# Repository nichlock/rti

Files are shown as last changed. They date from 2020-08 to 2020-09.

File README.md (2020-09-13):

# Open Source RTI

Source for the software, hardware and physical construction of a Reflectance Transformation Imager for George Washington University.

For information on the contents of the system, see [our Wiki](https://github.com/nichlock/rti/wiki). For more on the build and usage, [see the docs folder](../../tree/master/docs).

This repository contains our RTI's hardware and software implementation, and includes the source and documentation for:
1. A custom designed Arduino Mega shield to control the dome, which powers a three-color LED matrix and triggers the cameras.
2. Another custom circuit board which holds all three colors of LEDs in a smaller area than if we had three separate boards, allowing for a more compact dome.
3. The program to control the dome, with a serial or GUI control interface.
4. The GUI within the above program, which enables easy control over the whole system with no need for technical knowledge. See more about the GUI on our [system overview page](https://github.com/nichlock/rti/wiki/About-the-System#software-and-gui).

Image of the main dome

Image of the software's home screen.

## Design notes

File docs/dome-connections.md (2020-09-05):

### Contents

- [About the Wiring Scheme](#About-the-Wiring-Scheme)
- [How to Wire the Dome Matrix](#How-to-Wire-the-Dome-Matrix)
  - [Getting Parts](#getting-parts)
- [The Process](#The-Process)
  - [1. Get Things Together](#1-Get-Things-Together)
  - [2. Solder Wires on LED Boards](#2-Solder-Wires-on-LED-Boards)
  - [3. Install LED Boards](#3-Install-LED-Boards)
  - [4. Measure and Cut Wires and Build Connectors](#4-Measure-and-Cut-Wires-and-Build-Connectors)

---

# About the Wiring Scheme

If you're familiar with LED arrays, you can skip to [How to Wire the Dome](#how-to-wire-the-dome-Matrix).

## Common Matrices

When creating an array of LEDs, the common choice is to create a matrix of LEDs. This matrix allows us to control lots of LEDs with few control lines, meaning less hardware is needed to connect and drive the matrix. Matrixes are represented in rectangular configurations, but they can take any shape needed, and in our case, that shape is of circular rings that climb up a semi-sphere.

A commonality of RTI dome designs is to have 8 rings of 8 LEDs - and that's no coincidence. These domes are designed after an 8x8 LED matrix, which has 64 LEDs in it. One way to think of these matrixes is as a grid with units used to refer to any one position. The position (0, 0) is the first row, first column, while the position (5, 6) is the one cell that is both in the fifth column and sixth row.

Take a look at this picture. Although it may not look like a grid, it's got the same concept - the LEDs, represented with the arrow symbols, are all connected to exactly one column and one row. The columns and rows cross in this picture but they aren't connected. By "activating" column 5 and row 6, the LED at the position (5, 6) will turn on.

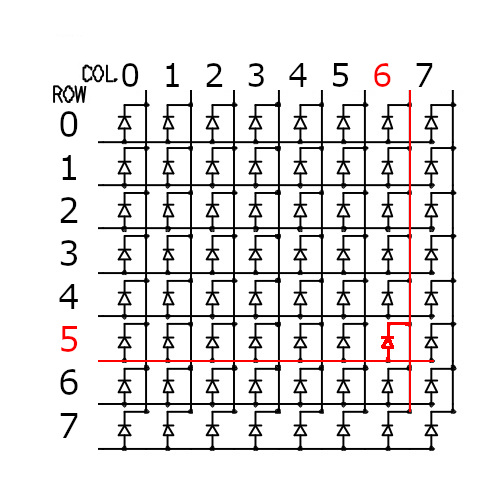
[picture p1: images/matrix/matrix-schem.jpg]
Matrix schematic
|  |
| :--- |
| (Original image credit to Arduino: https://www.arduino.cc/en/Tutorial/RowColumnScanning) |

Something to note about these is that in the real world, we can activate multiple LEDs in this matrix either one column at a time or one row at a time. If we tried to activate two LEDs diagonal to each other, say (0, 0) and (1, 1), we would end up with (0, 1) and (1, 0) also lit up.

## Our System

That's what it looks like for a single color array, but we need three colors: ultraviolet, white, and infrared. All we need is three more copies of the 8x8 design all connected - in three dimensions, you can think of stacking three 8x8 grids on top of each other. For all three stacked matrices, if the columns are kept as three separate groups of 8, the 8 rows can be connected across the layers, and we will still get a unique position for any coordinate. The position (0, 5, 6) will always be the LED in the first layer, sixth group of rows, and fifth column.

When we plug that in our schematic we can't use three dimensions, so we flatten it down. Looking at this image, notice that the only difference is that there are three LEDs for each LED before, and three additional corresponding columns.

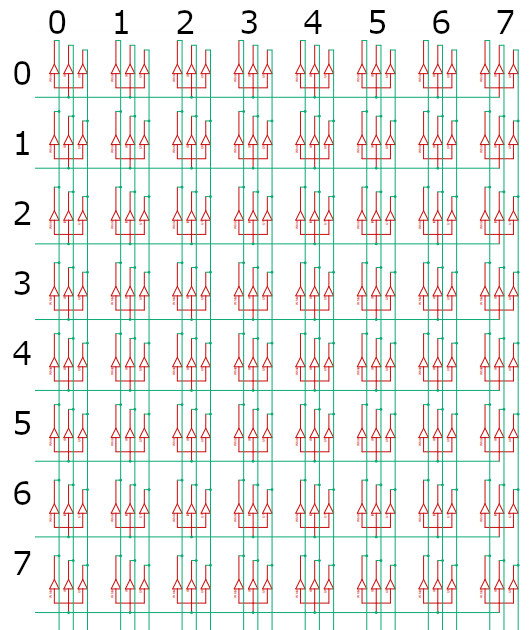
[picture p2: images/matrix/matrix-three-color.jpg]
An image of a three-color matrix


# How to Wire the Dome Matrix

Essentially, we are connecting the common cathode as the columns and the uncommon (separate color) anodes along with the rings. We wired it this way because connecting LEDs going up the columns requires more wire, so it needs fewer connections.

## Getting Parts

It is important to purchase the correct hardware, as the number of parts you'll need scales quickly. There are three important parts of the wiring:
- The wire
- The splice connectors
- The mounts for holding wires

### Wire

The wire needs to be a large enough gauge to handle the current without dropping the voltage. A drop in voltage will result in a dimmer LED, and the only controllable factors which can limit the voltage drop are **wire length** and **wire thickness**.

**Wire length**: To minimize wire length, connect the end of the wire that wraps around the dome back to the beginning of the wire.

**Wire Thickness**: Wire thickness depends mainly on what you can actually find to buy. Note that this depends on your selection of wiretaps.

### Splice Connectors

The splice connectors we used are wiretaps, which allow one wire to pass through while connecting another wire to it. Our specific choice was the Molex `19216-0003`.

### Mounts

In our design, the LED boards were attached with PVC tubes, which stuck out of the outside of the dome by a little over a centimeter. This worked perfectly well as a mounting mechanism, as the wires could just lay on the tubes. We also found that with how lightweight our wires and splices were, we didn't need mounts anyway. You should consider this in your design, though, as the wires will pull out of any connector with enough force.

# The Process

Finally, this was our procedure for connecting the dome.

## 1. Get Things Together

Start with the dome with all holes drilled and wiring tubes installed. The LED boards should be assembled, but not yet installed on the dome. You'll want the [connectors for the dome wiring](#building-connectors) and the [splice connectors](#Splice-Connectors).

## 2. Solder Wires on LED Boards

Wires that connect to the LEDs through the tubes are all cut at the predetermined length and soldered on the LED boards. See more in the [build guide](../../blob/master/docs/RTI%20Build%20Guide.pdf).

## 3. Install LED Boards

Install the LED boards by fitting the wires through the tube in the dome. Since we planned on modifying the LEDs, we used hot glue to attach them to the dome. The wires should be fairly tight and should not loop into the dome.

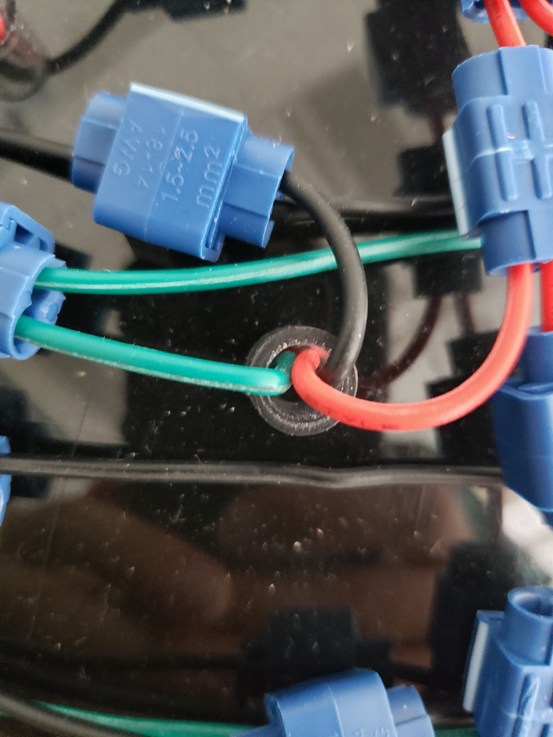
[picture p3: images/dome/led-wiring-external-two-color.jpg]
The wiring as viewed from outside the dome.
| The wiring as viewed from inside the dome. |  |
| :--- | :--- |
| An LED board installed, seen from inside the dome. This board was populated with UV and White LEDs, so it has three wires. | The view of the installed LED from the outside the dome. |

## 4. Measure and Cut Wires and Build Connectors

### Label Columns

Start by labeling the columns to help stay organized. This is temporary, so taped paper with the number written on it will do. 

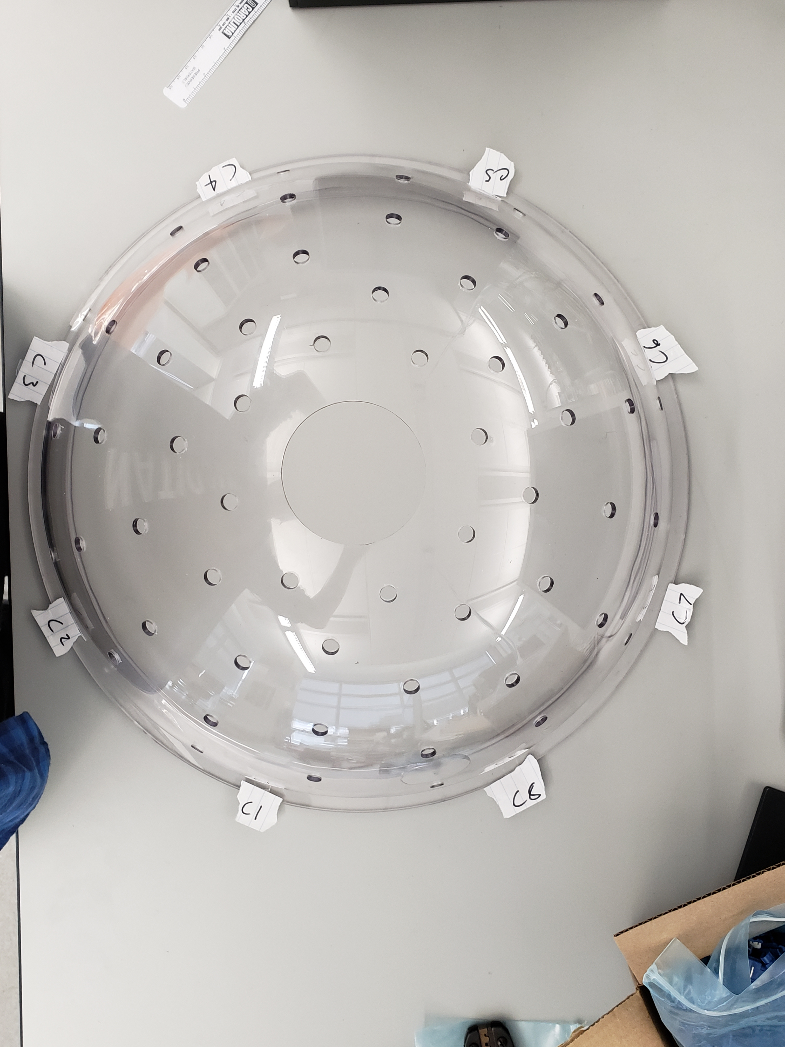
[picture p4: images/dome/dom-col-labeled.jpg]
The 8 columns all labled


### Measure and Cut the Column Wires

Unspool a length of wire, without cutting it, and [install the 9 cable splices](#Installing-Cable-Splices). Connect the end of the wire to the topmost LED on the first column. To use the splice connector, simply insert the wires fully and clamp down the metal plate so that it goes flush with the plastic, then close the plastic clip. Make sure the wires won't just fall out by tugging on them with low force (too much force will pull the wire out by stripping it). 

Connect the wire down the column to every LED on that column. When done, let the wire go to the bottom of the dome, and, with a large bending radius, bend the wire along the lip of the dome. Run the wire along the bottom of the dome until you get to where you want the connector. Give the wire an extra `4in/10cm`, and cut it.

The red wires and attached blue connectors in this image are essentially what you should be seeing:

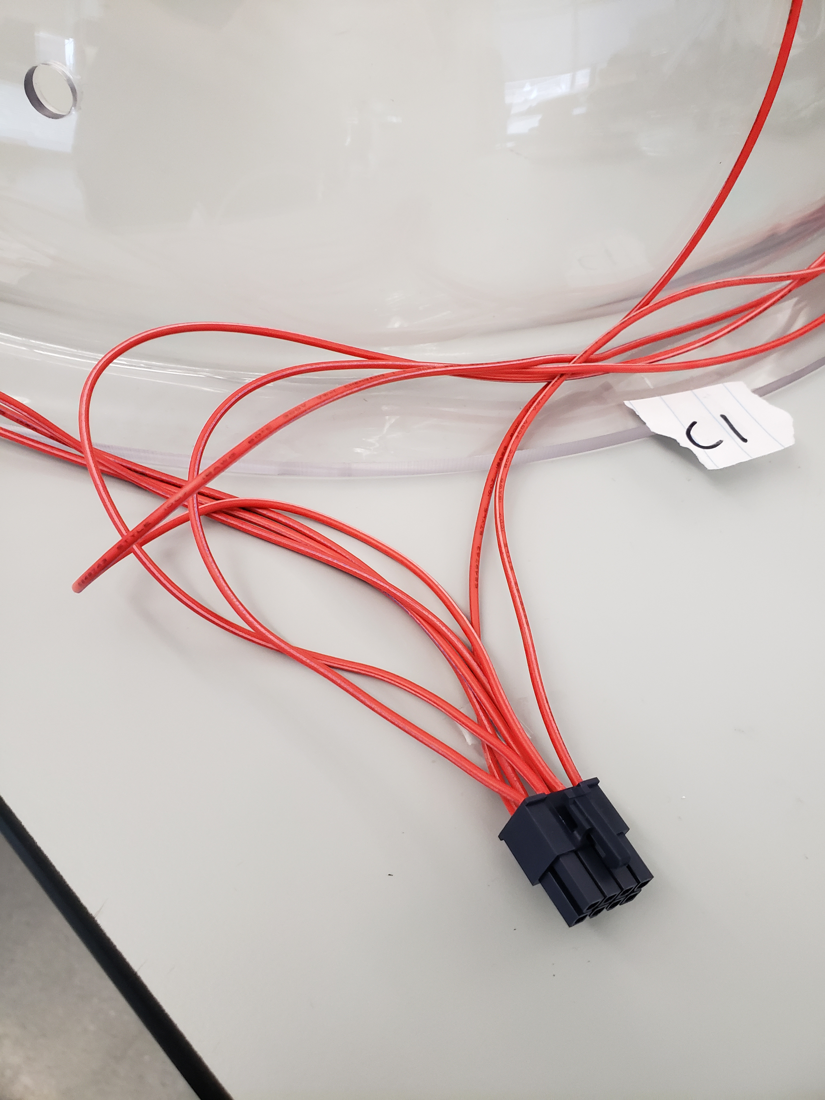
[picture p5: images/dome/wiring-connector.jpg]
Wires going to the connector
| Dome column connections |  |
| :--- | :--- |
| The connections made on the dome. For now, focus on the red wires central in the image and the blue connectors. | The column wires going into the connector. |

Crimp the wire and insert the pin into the connector. See [Building the Connectors](#building-the-connectors) below for more.

Repeat for all eight columns.

### Measure and Cut the Ring Wires

You'll need a set of 8 wires going around the dome for each fully populated color. Even if you don't need to populate all columns, it may be worth it to measure the wire and coil it up at the base of the connector if you plan on adding it later. Start with a color you don't plan on adding more of, though, since that set of wires will then be beneath all others.

Unspool a length of wire, without cutting it, and [install the 9 cable splices](#Installing-Cable-Splices). Start at the bottom ring of the final column. With the end of the wire pointing to the first column, connect the LED wire to the one you are installing. Leave enough extra wire to connect the wire to itself when it comes back around since that will reduce power losses.

Go around the dome connecting the LEDs, laying the wire on top of the tube if needed. The wire should have enough slack that it won't be a challenge to run a wire under it. 

Once you wrap the wire fully around, connect the open end of the wire to the side of the wire you're working on using the final splice. Run the wire down the area between the final column and the first column, give the wire an extra `4in/10cm`, and cut, crimp, and install it in the connector. See [Building the Connectors](#building-the-connectors) below for more.

### Installing Cable Splices

TODO: this should cover using the cable splices, and how to install them when starting a column or ring.

### Building the Connectors

TODO: Should describe stripping, crimping, and inserting a wire into the 8-pin connectors.

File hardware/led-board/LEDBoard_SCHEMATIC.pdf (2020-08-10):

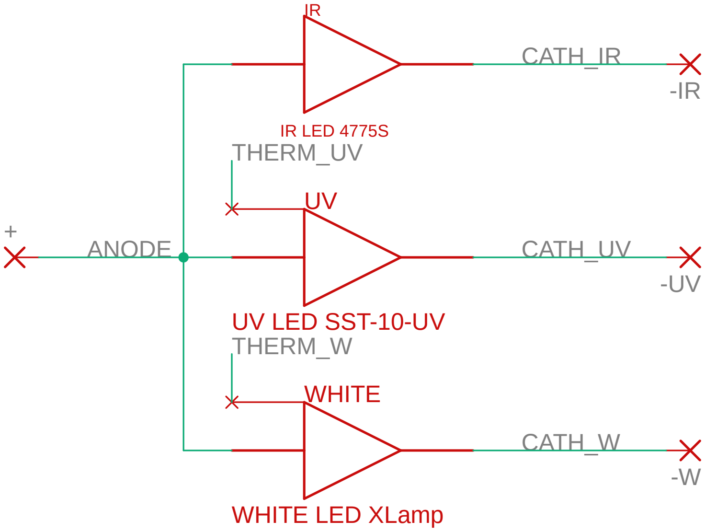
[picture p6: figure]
ANODE; CATH_IR; CATH_UV; CATH_W; THERM_UV; THERM_W; IR LED 4775S; UV LED SST-10-UV; WHITE LED XLamp; WHITE

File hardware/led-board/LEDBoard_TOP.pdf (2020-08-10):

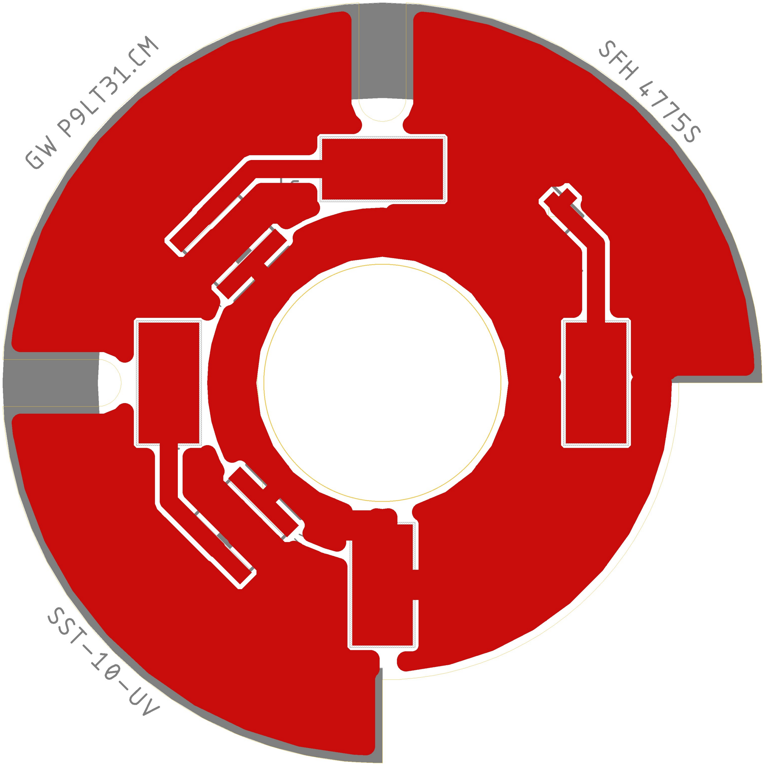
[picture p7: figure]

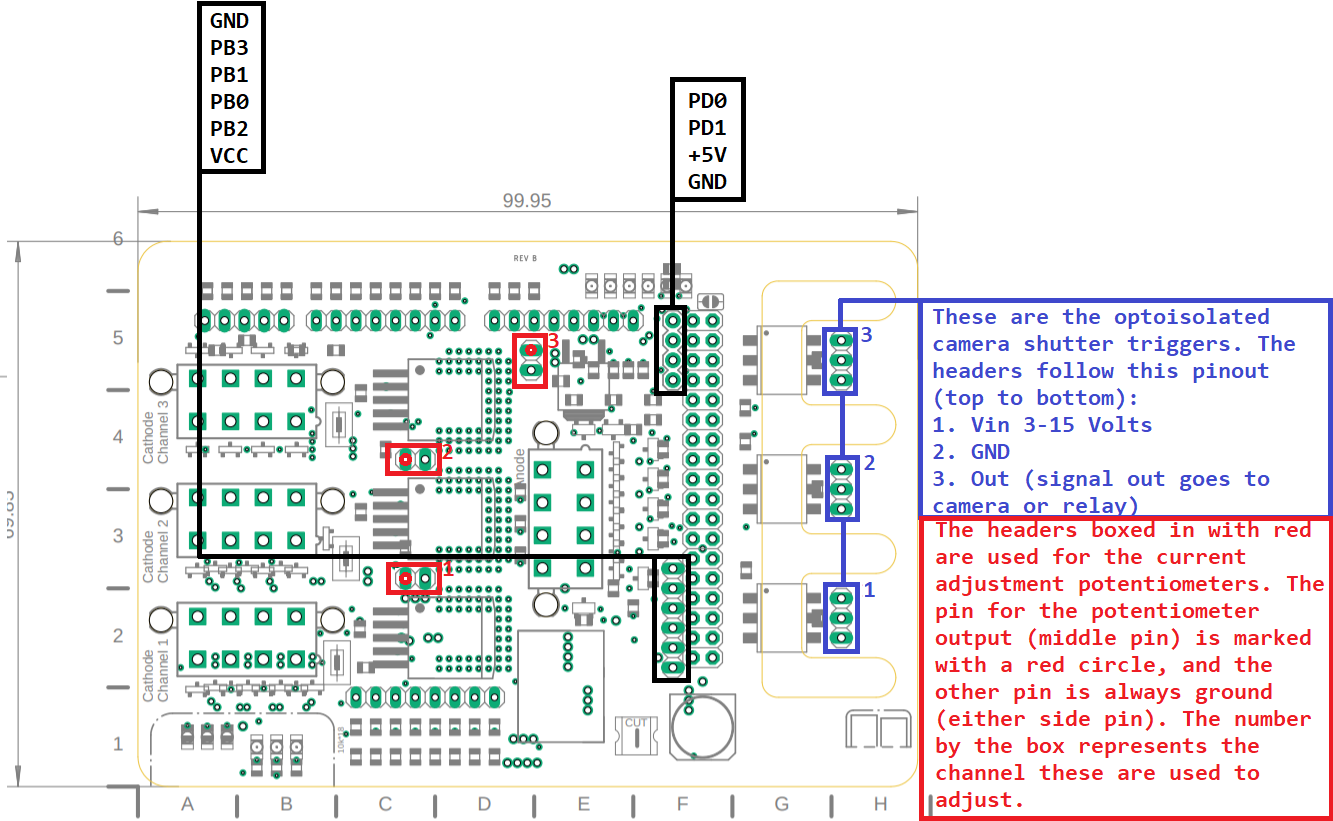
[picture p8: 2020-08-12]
images/driver-shield/pinout.png

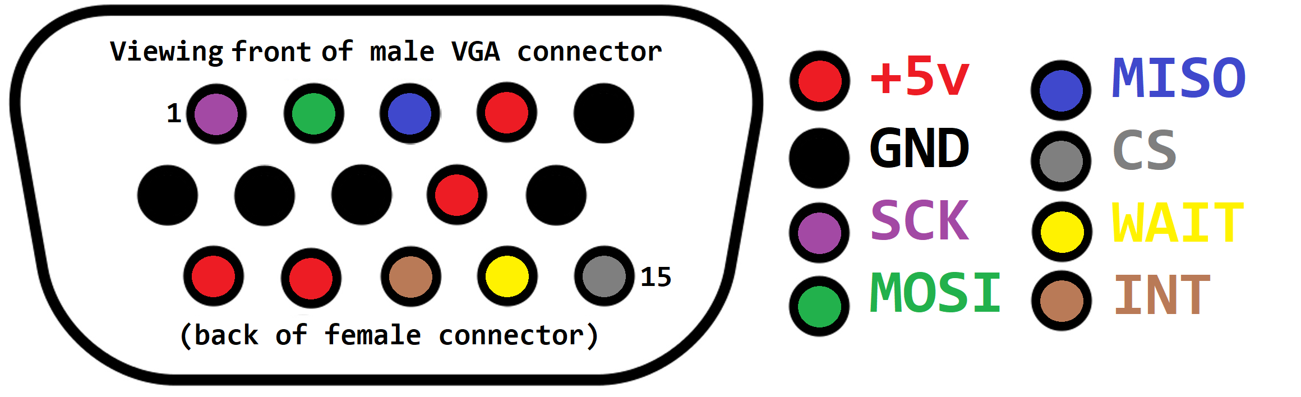
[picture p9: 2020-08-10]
hardware/VGA Diagram.png

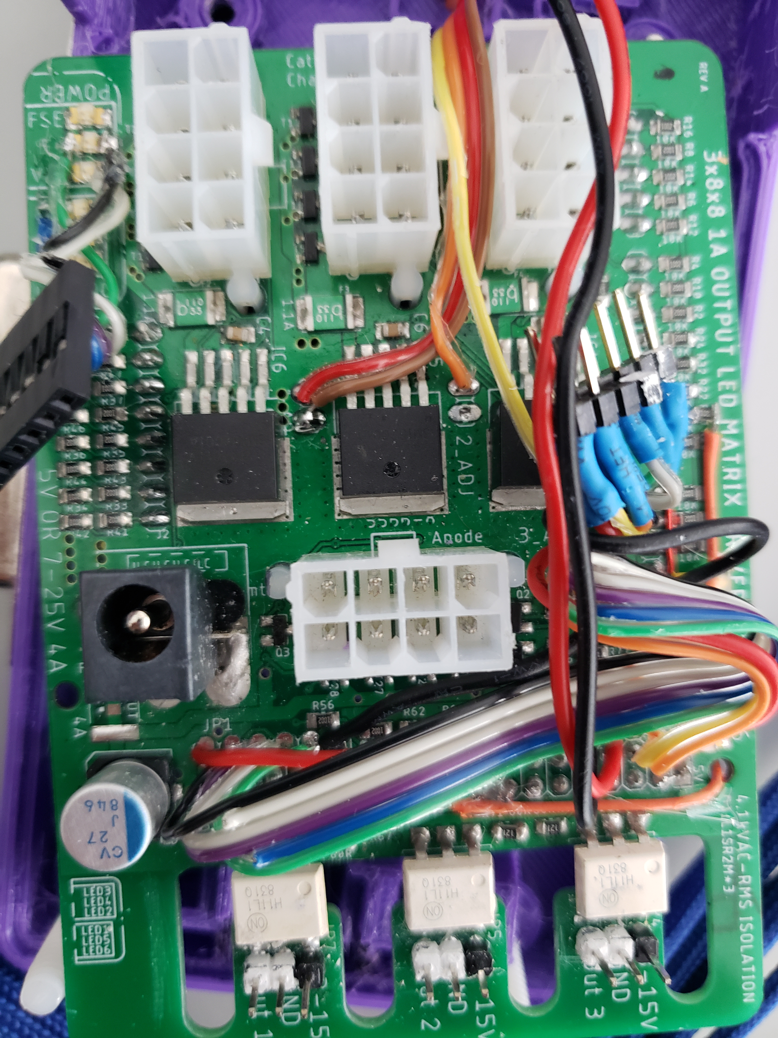
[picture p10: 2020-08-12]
images/driver-shield/top-populated.jpg

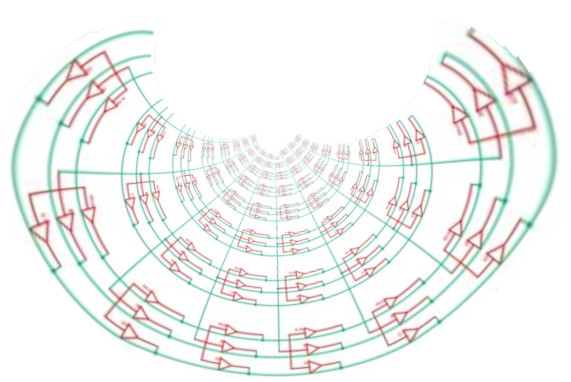
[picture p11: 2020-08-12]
images/matrix/matrix-three-color-no-label-warped.jpg

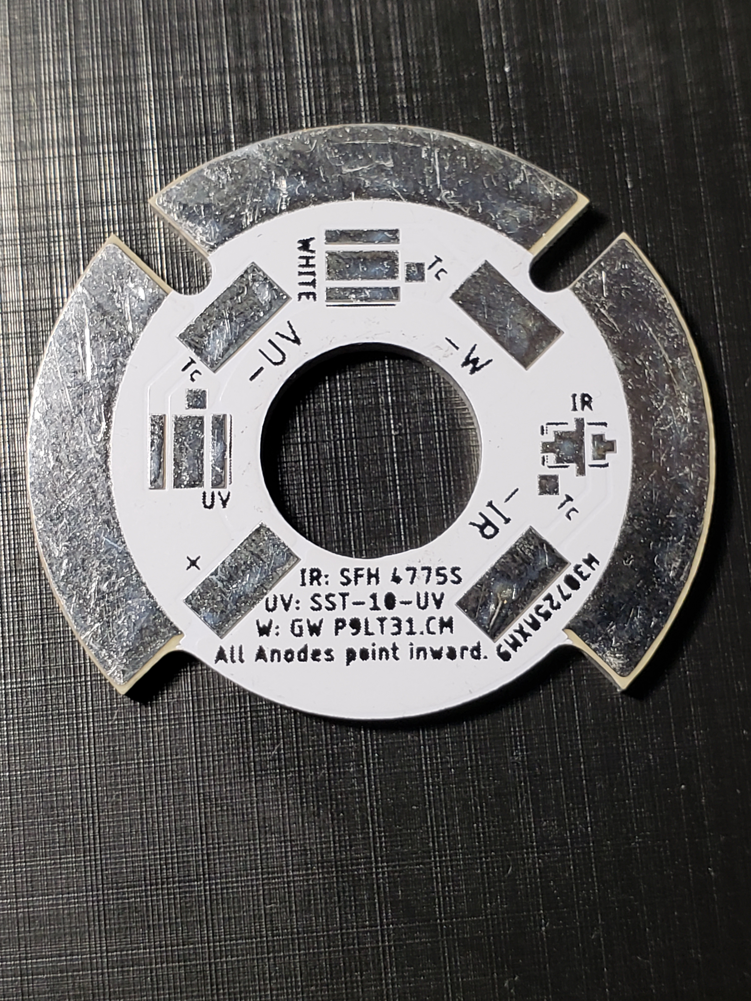
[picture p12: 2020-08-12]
images/led-board/full-unpopulated-led-board.jpg

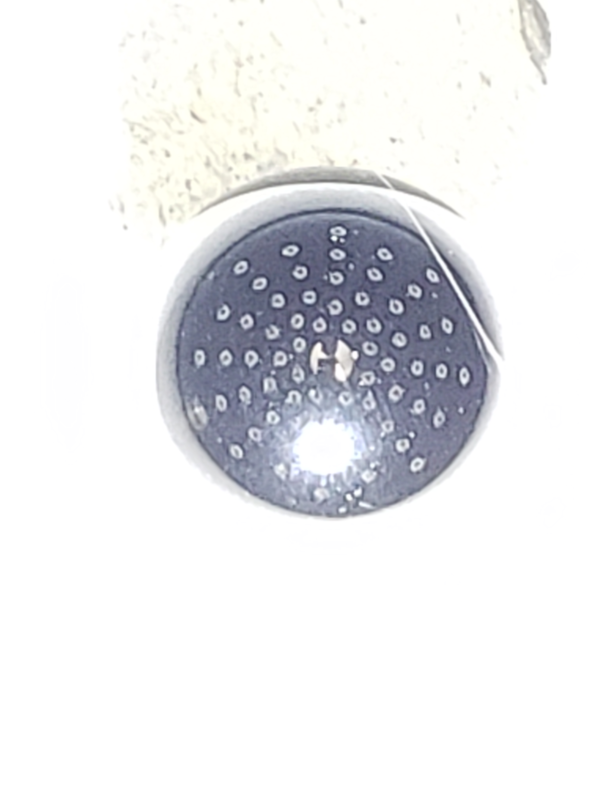
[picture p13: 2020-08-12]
images/dome/ceramic-ball-reflections.jpg

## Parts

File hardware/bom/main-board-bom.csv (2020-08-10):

Part | Info | # | CPU at quantity* | Line cost | Mouser P/N | Digikey P/N | MFR ID | Notes | Optional?
Passive Components |  | 100 |  | 14.636
Resistors | 10k | 64 | 0.069 | 4.416 | 71-CRCW080510K0FKEAC |  | CRCW080510K0FKEAC | Used on mosfets
 | 560R | 4 | 0.1 | 0.4 | 71-CRCW0805560RJNEB |  | CRCW0805560RJNEB | CAT4101 Adjustment Resistors AND one 12v LED current limit resistor
 | 175R | 4 | 0.1 | 0.4 | 71-CRCW0805-178-E3 |  | CRCW0805178RFKEA | 5v LED current limit resistors
 | 60R | 3 | 0.1 | 0.3 | 71-CRCW080556R0JNEA |  | CRCW080556R0JNEA | H11L1MS Protection Resistors
Resettable SMD fuses | 3.5A - 4A | 0 | 0.57 | 0 |  | RGEF400HF-ND | RGEF400 | Main fuse | Not used in design, but it is still an option. Item not included in final price or component count.
 | 1.1A | 3 | 0.27 | 0.81 | 530-0ZCG0110CF2B |  | 0ZCG0110CF2B | CAT4101 channel fuses
Power Capacitor C7 | 100uF | 1 | 2.97 | 2.97 |  | 493-4561-1-ND | PCV1J270MCL7GS | Decoupling cap, needed for long power cables. | Use if power cables are long as it will dampen the effect of a sudden supply or voltage drop.
Capacitors | .1uF | 7 | 0.1 | 0.7 |  | 1276-1007-1-ND | CL21F104ZBCNNNC | CAT4101, 7805, and H11L1MS decoupling capacitors | Three capacitor allocated to H11L1MS decoupling are only needed it is used. One capacitor is for the 7805 regulator.
 | .33uF | 1 | 0.22 | 0.22 |  | 1276-6813-1-ND | CL21B334KBFVPNE | 5V linear regulator cap | Only purchase if 7805 is used.
LEDs |  | 4 | 0.34 | 1.36 |  | 160-1456-1-ND | LTST-C230KGKT | Power Supply Indicator LEDs | Optional. Useful for troubleshooting.
 |  | 9 | 0.34 | 3.06 |  | 160-1456-1-ND | LTST-C230KGKT | Active color and position indicator LEDs | Optional. Useful for troubleshooting.
Active Coponents |  | 47 |  | 31.9
N-mosfets |  | 24 | 0.46 | 11.04 | 726-BSS306NH6327XTSA |  | BSS306NH6327XT | Cathode driver mosfets
P-mosfets |  | 8 | 0.76 | 6.08 | 781-SI2319DS-GE3 |  | SI2319DS-T1-GE3 | Anode driver mosfets
NPN transistors |  | 8 | 0.11 | 0.88 | 863-BC849BLT1G |  | BC849BLT1G | Used to control P-mosfets
CAT4101 |  | 3 | 3.21 | 9.63 | 698-CAT4101TV-T75 |  | CAT4101TV-T75 | LED constant current driver
7805 Linear Regulator |  | 1 | 0.58 | 0.58 | 863-NCV7805BDTRKG |  | NCV7805BDTRKG | 5v linear regulator | Optional if a built in linear 5V power supply is needed. Required if a 5v supply is not provided.
H11L1MS |  | 3 | 1.23 | 3.69 |  | H11L1SR2MCT-ND | H11L1SR2M | Opto-isolated shutter controls | Not always needed, but don't skip out on it unless you have a specific reason. Not having these could lead to some costly mistakes!
Connectors |  | 11 |  | 7.53
ATX 8 pin male | 2R, 8P | 4 | 1.08 | 4.32 | 571-1775099-5 (cheaper alt.) | WM17748-ND | 39-30-6087 | Connects to LEDs
Barrel Jack | 2.1mm | 1 | 1.15 | 1.15 |  | CP-006APJCT-ND | PJ-006A-SMT-TR | Power supply connector, rated up to 4A.
Male Headers | 24 pos | 2 | 0.46 | 0.92 |  | S1012EC-24-ND | PREC024SAAN-RC | Break headers up into 3 twos, 3 eights, a four, a five, and a six.
Dual Row Male Headers | 2R 36P | 1 |  | 0 |  |  |  | For Arduino MEGA conection
Female Headers | 3 pos | 3 | 0.38 | 1.14 |  |  |  | For use with H11L1MS output.
Total for circuit board |  | 158 |  | 54.066
External Parts |  | 301 |  | 38.1216
Inline tap wire connector |  | 256 | 0.1288 | 32.9728 |  | WM18735-ND | 19216-0003 | Used to branch out hookup wire on the dome. | These are the easiest and cheapest solution we found. If time is not an issue, the wires could be soldered at virtually no monetary cost.
Crimp-on female ATX pins |  | 32 | 0.1034 | 3.3088 | 538-43030-0038 | WM13070CT-ND | 430300038 | Inserted into ATX 8-pin female housings | If the ATX 8 pin male connectors aren't used on the circuit board, it is not needed.
ATX 8 pin female housings |  | 4 | 0.46 | 1.84 |  | WM16167-ND | 469920810 | Plugs into circuit board | If the ATX 8 pin male connectors aren't used on the circuit board, it is not needed.
Standoffs - Not included |  | 3 |  | ? |  |  |  | Standoffs can be found at a hardware store and may be cheaper there.
Screws - Not included |  | 6 |  | ? |  |  |  | Screws can be found at a hardware store and may be cheaper there.
VGA Cable |  | 1 |  |  |  |  |  | Used to connect display to main board
VGA Connectors - Male |  | 2 |  |  |  |  |  | As above.
Total Electrical, w/o LED parts |  | 459 |  | 92.1876
*Price determined at time of purchase of original prototype purchase.

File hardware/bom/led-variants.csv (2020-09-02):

Product Code |  | half angle | I-max mA | Vf @1A, 25°C | Wavelength | Radiant Flux @1A | Notes/URLs
Infrared 800 - 1200nm |  |  |  |  |  |  | None used in original design.
SFH 4725S |  | 40 | 1A | 2.7 | 945 | 500 - 1280 mW/sr
SFH 4775S |  | 60 | 1.5 | 2.7 | 945 | 900-1800 mW/sr
White | CRI for Listed Ratings |  |  |  | Warmth | Lumens @ 25°C
XLamp XP-G2 | 90 CRI | 60 | 1500 | 2.9 | 2700-3000K | <360
XLamp XP-G2, High Efficacy | 90 CRI | 65 | 2000 | 3 | 2700-6200K | <315
DURIS® S 8, GW P9LT31.CM | 95+ | 60 | 1800 | 2.9 | 2700-4000K | <315
XPGBWT-UE-0000-00GE2 | 90 CRI | 60 | 1500 |  | 5700K | 143
XPGBWT-UE-0000-00DE4 | 90 CRI | 60 | 1500 |  | 4500K | 118
XPGBWT-UE-0000-00CE8 | 90 CRI | 60 | 1500 |  | 2700K | 110
XPGBWT-UE-0000-00DE5 | 90 CRI | 60 | 1500 |  | 4000K | 118
XPGBWT-UE-0000-00CF6 | 90 CRI | 60 | 1500 |  | 3750K | 110
XPGBWT-L1-0000-00GE3 | 75 CRI | 60 | 1500 |  | 5000K | 143 | Used in original design.
Ultra-Violet 315 - 400nm (UV-A)
Luminus SST-10-UV-A130-E365-00 |  |  | 500 |  | 385+ | 1.62mW | Flux is in Radiometric Flux, see Datasheet for more info. Used in original design.

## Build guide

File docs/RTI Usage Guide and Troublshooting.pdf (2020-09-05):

### RTI Usage Guide/Information

Home screen menu
- LED Order - Enters the menu used to run the LEDs on the dome in a pattern.
- LED Single - Used to run LEDs on the dome individually.
- Settings - Change settings or restart the device (more settings are made available by connecting to the device from the USB serial connection offered by the Arduino.
- Profiles
- Write to the on-board timing profiles which can be used while running LEDs in either single mode or pattern mode
- Test LEDs
- Performs an automatic test on the LEDs.
- Positions
- Allows the user to save custom LED configurations on the dome, which are used to skip non-populated LEDs when using a pattern.

LED Order
From this page, the desired LED Pattern Type must be selected. The options are as follows:
- Column Scan: Runs LEDs column by column, going from top to bottom. (This order follows the designed numeric order of the LEDs).
- Ring Scan: Runs LEDs ring by ring, starting at the top ring and going down.
- Single Column: Runs an individual column, beginning at the top of the column and running - down it. (One column, as defined by this software, is actually two adjacent lines of LEDs. See diagrams below.)
- Single Ring: Runs an individual ring, starting at the lowest numbered LED in that ring and going around counter-clockwise.
After a Pattern Type is chosen, a page is shown with many different setting selectors. The boxes are divided into LED and Shutter settings. To change any setting, tap on it’s box. These settings may have been pre-defined using the Profiles setup page; if this is the case, tap the boxes labeled ‘Profile:’ and choose the correct profile from the dropdown box.
To change a setting manually, tap on its box and either choose the desired option from the dropdown or type the setting on the number pad which appears in the space to the right. LED Setting Definitions:
- Profile - use a predefined profile to automatically set up the settings.
- Color - change the color which the system should use for the pattern.
- On Time - The amount of time the LED will remain on.
- Off Time - The delay between turning off the last LED and turning on the next one.
- Increment - This is used to reduce the time the entire process will take, at the cost of a lower image count. The pattern will be run by running each n

th LED (an increment of two uses every second LED, making it take half the images, while an increment of eight will run every eighth LED, taking an eighth the images.)

Shutter Setting Definitions:
- Profile - use a predefined profile to automatically set up the settings.
- On Time - This will be the maximum amount of time the shutter is left on. (it is initially set up as the minimum time since the user will be warned if the shutter cannot stay on this long)
- Trigger w/ - Select the logical level at which the camera triggering system is activated. (some cameras may take an image while the signal is ‘high,’ or on, while others will activate when the signal is ‘low,’ or off.)
- NOT VISIBLE: Starting Delay - The amount of time the shutter waits before turning on after the LED has been activated. This is preset in the shutter profile. If none is set, it will default to .1 seconds.

The LED On Time should be enough to accommodate the Shutter On Delay and the Shutter On Time, otherwise the display with show an error (though the pattern can still be run if it's just for a test).
If no error appears, there will be a list of the numbers of the LEDs which will run. This list can be copied directly from the USB Serial connection on the Arduino in a comma-separated-value format. (In a Column Scan without any change in the Increment value, the LEDs will light in numeric order.)
The timing of the LEDs and the camera shutter depends upon the values set for the LED On Time, the Shutter Wait Time, and the Shutter On Time (and are offset by the LED Off Time, if used.) The shutter will be turned on once the LED has been turned for the duration of the Shutter Wait Time. The shutter will then turn off after the amount of time set in the Shutter On Time has passed. Regardless of the Shutter On Time, the shutter will always be turned off when the LED is off.

An overall time estimate is given below the list on the display. This is only an estimate, and maybe slightly inaccurate at larger numbers, but should not be off by more than a few seconds.
When the Start button is pressed, a box will appear with information about the current LED pattern being run. There are two numbers used to identify LEDs: the LED Number and the Dome LED Number. The LED Number is a zero-inclusive value representing the logical position in the program’s array, and the Dome LED Number is a zero-exclusive value representing the physical position of the LED on the dome. This can be compared to the Single LED selector but remember to subtract one from this value first to make it zero-inclusive.

LED Single
When opening this page, some instructions will appear, which can be passed by tapping the display.

Once the page is shown, there will be a few buttons to the left and an LED selector grid on the right.
The LED selector grid is a visual way to choose which LED should be turned on. The LEDs also have numbers written over them, which are also displayed at the bottom left of the window when an LED is on (labeled Dome LED number). Both numbers in the counters are zero-inclusive. The graphic has a white circle to one side, which indicates the hole drilled in the side of the dome (when it is viewed from the top).
Before choosing an LED, make sure the correct color is selected from the right. The color-filled buttons to the left can be used to change the LED color. The top-most white-filled button is used to select a pre-created shutter profile to use when LEDs are enabled, and the bottom-most button is used to change the shutter’s “Trigger With” setting.

Settings
The Settings page only contains three settings, which are all toggle buttons.
- The first button, Diagnostics, is used to enable drawing and writing circles and general running information to the display. More information can be found in the header of the program file ‘main.cpp’
- The second button is a restart button, which just restarts the device. Useful for troubleshooting and programming.
- The calibrate display button begins the display touch location calibration, which only requires that the user touches two locations on the display. If the display is not usable due to an issue with the calibration, this must be done through the USB Serial connection.
- The button labeled Combine Shutters is used to control all three camera color shutter outputs in unison, regardless of the color being used. Since there are three colors, all three camera control shutters can be used separately if preferred, though this can be an issue if a camera is not connected to the correct shutter.

Profiles
To add or modify a profile for a pattern, follow these steps:
1. Tap on the pattern name on the screen. To add a profile to all patterns, tap “All Patterns”.
2. Choose which profile you would like to write to. Patterns have three profiles each. The profiles can be overwritten if needed.
a. If you are modifying all pattern profiles at once, the profile number will be the same within all profiles (if profile #2 is selected, the second profile will be written to in all pattern profiles, and will overwrite any settings previously saved there.)
3. Enter the name of the profile.
4. After the name is set, a new screen will appear, with instructions on the left and a keypad on the right. Enter the settings you wish to apply to the profile.
5. Once complete, the keypad will disappear and you can return home. The profile is automatically saved.

To modify a profile for the camera shutter settings, follow these steps:
1. Tap the “Shutters” option.
2. Choose which profile you would like to write to. Eight shutter profiles can be saved. Profiles can be overwritten if needed.
3. Enter the name of the profile.
4. After the name is set, a new screen will appear, with instructions on the left and a keypad on the right. Enter the settings you wish to apply to the profile.
5. Once complete, the keypad will disappear and you can return home. The profile is automatically saved.

Test LEDs
Not yet implemented; this will test all LEDs automatically, using a photoresistor or photovoltaic sensor.

Positions
It may be necessary to limit one of the color arrays to only use certain LED positions, since some array positions may not be populated. To modify, enable, or disable one of these custom LED arrays, open the “Positions” menu option and select which channel/color you would like to limit.
Once you have chosen the color, a selector grid will come up, identical to the one used on the Single LED page. The graphic has a white circle to one side, which indicates the hole drilled in the side of the dome (when it is viewed from the top). The LED numbers are also shown on top of the circles they are represented by.
To set an LED to usable or unusable, tap on the LED’s circle so that it turns green or red, respectively. While setting the LEDs, all can be set to usable or unusable to speed up the process, using the “All On” or “All Off”.
Once the custom array is set up, press “Save”. The array will not be stored anywhere if it isn’t pressed. If desired, the custom array can be ignored but still saved using the “USE ARRAY?” toggle button.
NOTE: LEDs that are set to unusable will not be used when using the LED Order page to activate LEDs, but the position can still be powered when using the LED Single page.

Touch Calibration
The touch calibration screen can be activated by entering the Settings page and tapping the “Recalibrate Touch” button, holding the calibration reset button on the case, or by entering the device’s serial control interface. If the touch calibration is slightly off, the device will still be largely usable but will be especially difficult when using the individual LED selector.
When tapping the red target circles while calibrating, it is important to be as accurate as possible. Quickly and tap and release using something with a small end or corner, being careful not to accidentally lay a finger or palm on the rest of the display. The backside of a pen, the corner of a USB connector, or the tip of a headphone wire’s connector (3.5mm barrel connector) work well. Using a finger won’t be as accurate, but it will still work.

Touch calibration accuracy can be checked by enabling the “Diagnostics” setting in the Settings page and seeing how closely the circles appear to each tap. These circles are drawn wherever a touch is thought to have occurred. If no circles appear, the circles will likely be placed in one of the four corners due to bad calibration values.

Joining Shutters
There are three camera triggering outputs, called shutters. These can be used separately or can be joined so that all three outputs will trigger any connected camera when any LED channel is turned on. When shutters are joined, all three outputs will use the same shutter profile. This can be toggled in either the serial control interface or the settings control page. Joining shutters can also be used in case a shutter output is somehow broken, as was the case in our version.

Serial Interface
This device has a USB serial connection available through the Arduino library package. The default baud rate is 115200. The baud rate can only be changed through the serial connection. Disable newlines in the console if necessary - the interface will be buggy if you don’t.
The serial connection can be used to change settings not available in the display interface, change internal names, and run LED tests without the display. It can also be used to diagnose problems. When in the serial interface, you can press ‘h’ to show a help menu to help navigate the system.

Settings/troubleshooting options available through the serial connection:
- Reset serial baud rate (sets to 115200)
- Reset display touch calibration
- Reset channel/color names
- Change the serial baud rate
- Change channel/color names
- Toggling the verbose serial output
- Show free RAM
- Turn on patterns of LEDs or manually activate individual LEDs, one at a time.
- Resetting some settings saved in EEPROM. Resets serial baud rate, shutter joining, touch calibration values, display diagnostics mode, usage of custom arrays (which stops using arrays, but does not erase them,) and verbose serial.
- Resetting all data saved in EEPROM. This will erase profiles, all settings, display calibration values, and custom arrays, and will reset channel names and the serial baud rate. Only perform the clean erase if it is absolutely necessary.

### Troubleshooting

Display Troubleshooting
No Image:

- Reseat cable.
- See if the ‘Pin 13’ LED on the Arduino Mega board is toggling when tapping
- If not, then there may be an issue with the connection/cable.
- Try a more powerful power supply for the mainboard
- It is possible that there is too much of a voltage drop from the power supply to the display. (This actually has more to do with the wires of the power supply, but a more powerful one will likely have thicker wires.)
- Test backlight
- Use a bright light on the display and see if any image is barely visible. Point light at the top left/right corners and see if the blue border at the top of the display is there.
- See if the black screen changes at all in tone or color on power-up, indicating that there is power, but no image sent to the device.
- Check connector for continuity
The screen has light, but no clear image:
- Reseat cable.
- Check cable.
No touch control:
- Reseat cable.
- Try re-calibrating through the serial

LED Troubleshooting
Single LED not lighting:
- Run a baseline test (like a ring or column scan) with a skip of ‘1’ and see if the problem persists.
- Test LED using the Single LED function.
- If it lights, check the Positions menu to make sure the LED is not disabled.
- Reseat 8-pin LED connectors.
- Turn current to the minimum amount, test LEDs again, or unplug the potentiometers and see if the LED lights very dimly.
- If this works, the power supply may not be sufficient.
- Check connections on current adjustment potentiometers
- If the connection is intermittent, try reseating. If still intermittent, new parts may be needed.
- Shorting all four connectors together will also work, which will run the LEDs at full power.
- Make sure the power indicator LEDs are steadily lit when trying to light power LEDs.
- If the LEDs flicker, the power supply is not sufficient.
- Pinch/move around the blue inline splices on the dome, see if the connection is intermittent.
- Try moving the LEDs to a different channel. Be careful when changing channels: some LED colors may require a lower maximum current! If you aren’t sure, set all channels to minimum current while running device.

- Check voltage/current to LEDs manually.
LED Ring/Column is not lighting:
- Try activating LEDs in Single LEDs function. Check that the LEDs are not disabled in the positions menu.
- Reseat 8-pin connectors.
- Pinch/move around any blue connectors for the ring/column and see if the connection is intermittent.

### Known Issues

- When controlling single LEDs, setting a shutter profile may switch to the last channel. Channel can be changed back after it is accidentally set.

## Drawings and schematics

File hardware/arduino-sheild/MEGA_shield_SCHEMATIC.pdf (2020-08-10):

# ANODE CONTROL

10K | GND | Si2319DS

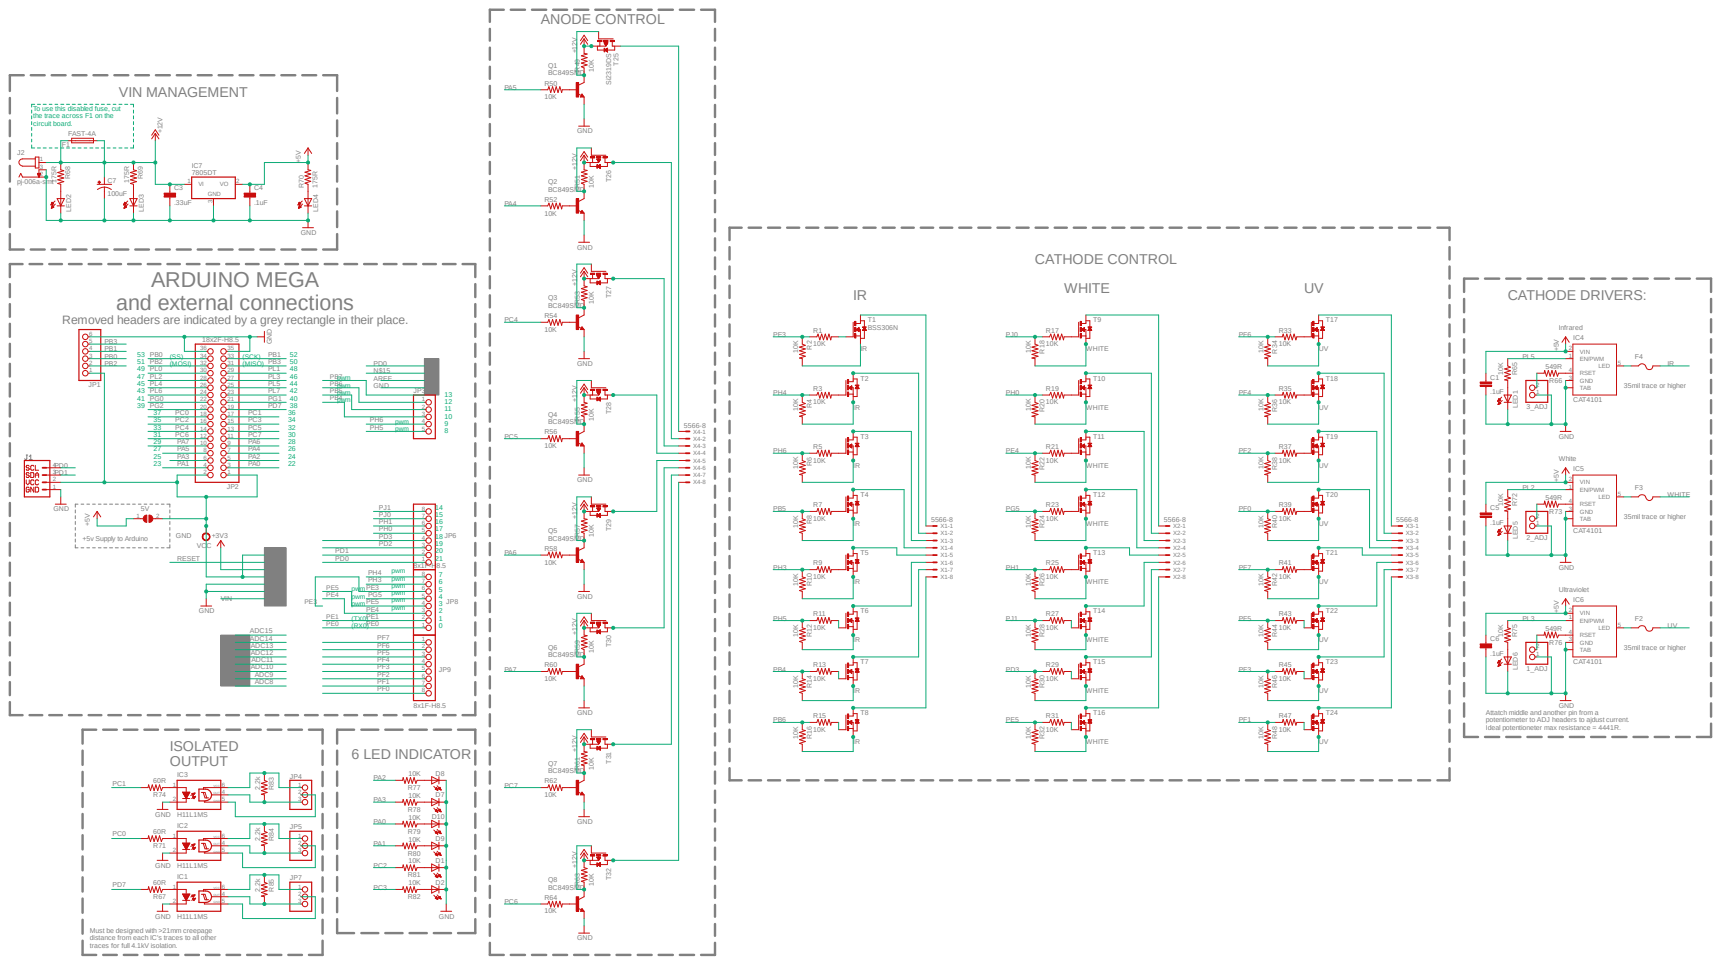
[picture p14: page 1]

10K GND GND GND ¹⁷⁵R

To use this disabled fuse, cut
the trace across F1 on the circuit board.

CATHODE CONTROL GND Must be designed with >21mm creepage
ARDUINO MEGA

Ideal potentioneter max resistance = 4441R. +5v Supply to Arduino Removed headers are indicated by a grey rectangle in their place.

549RGND
35mil trace or higher

Attatch middle and another pin from a
potentiometer to ADJ headers to ajdust current.

distance from each IC's traces to all other
traces for full 4.1kV isolation.

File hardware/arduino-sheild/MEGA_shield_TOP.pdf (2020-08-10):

6

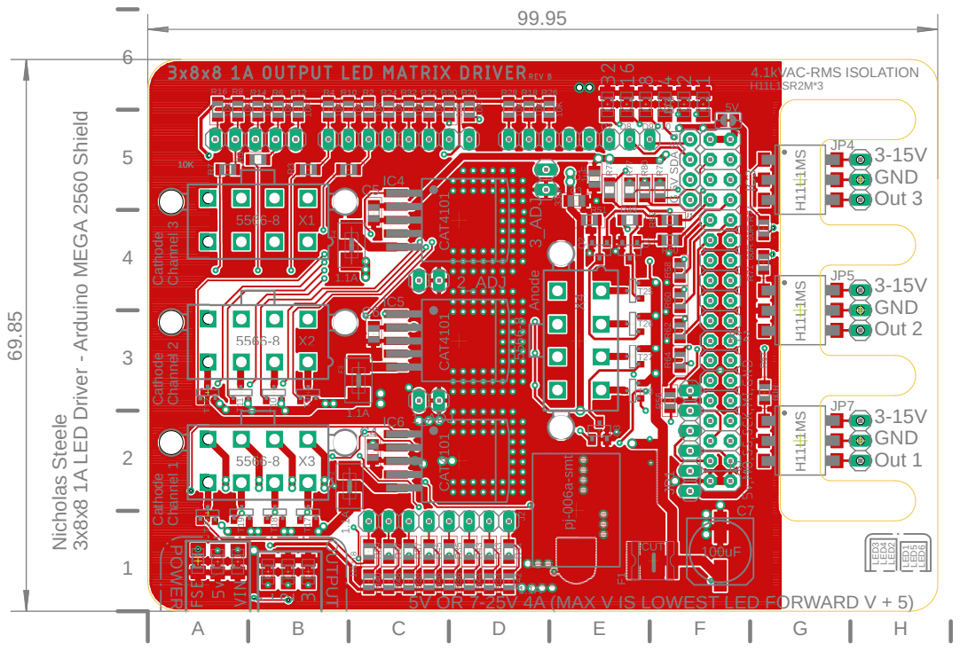
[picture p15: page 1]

99.95 Cathode Channel 1 Cathode Channel 2 Cathode Channel 3

4.1kVAC-RMS ISOLATION POWER Nicholas Steele 3x8x8 1A LED Driver - Arduino MEGA ²⁵⁶⁰ Shield

5V OR 7-25V 4A (MAX V IS LOWEST LED FORWARD V + 5)

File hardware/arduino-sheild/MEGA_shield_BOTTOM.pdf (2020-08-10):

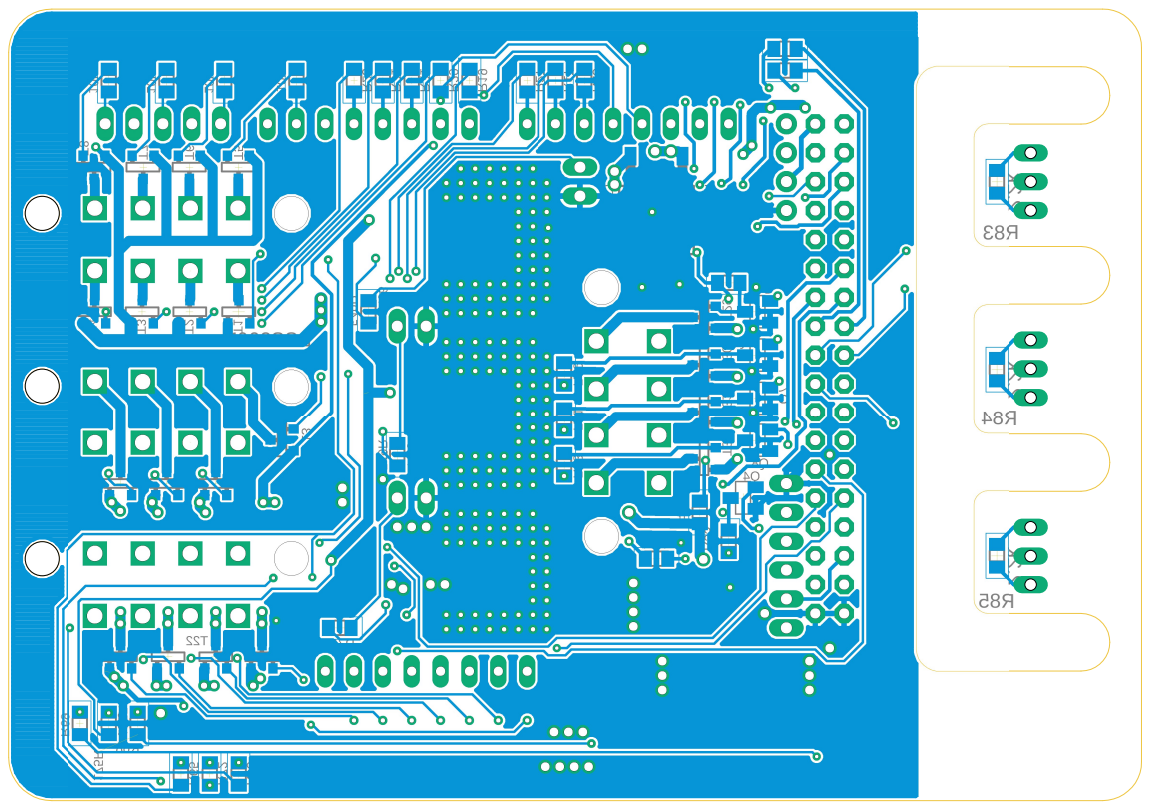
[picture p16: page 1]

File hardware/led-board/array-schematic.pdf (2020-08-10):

# W1 W2 W3 W4 W5 W6 W7 W8

## IR1 UV1

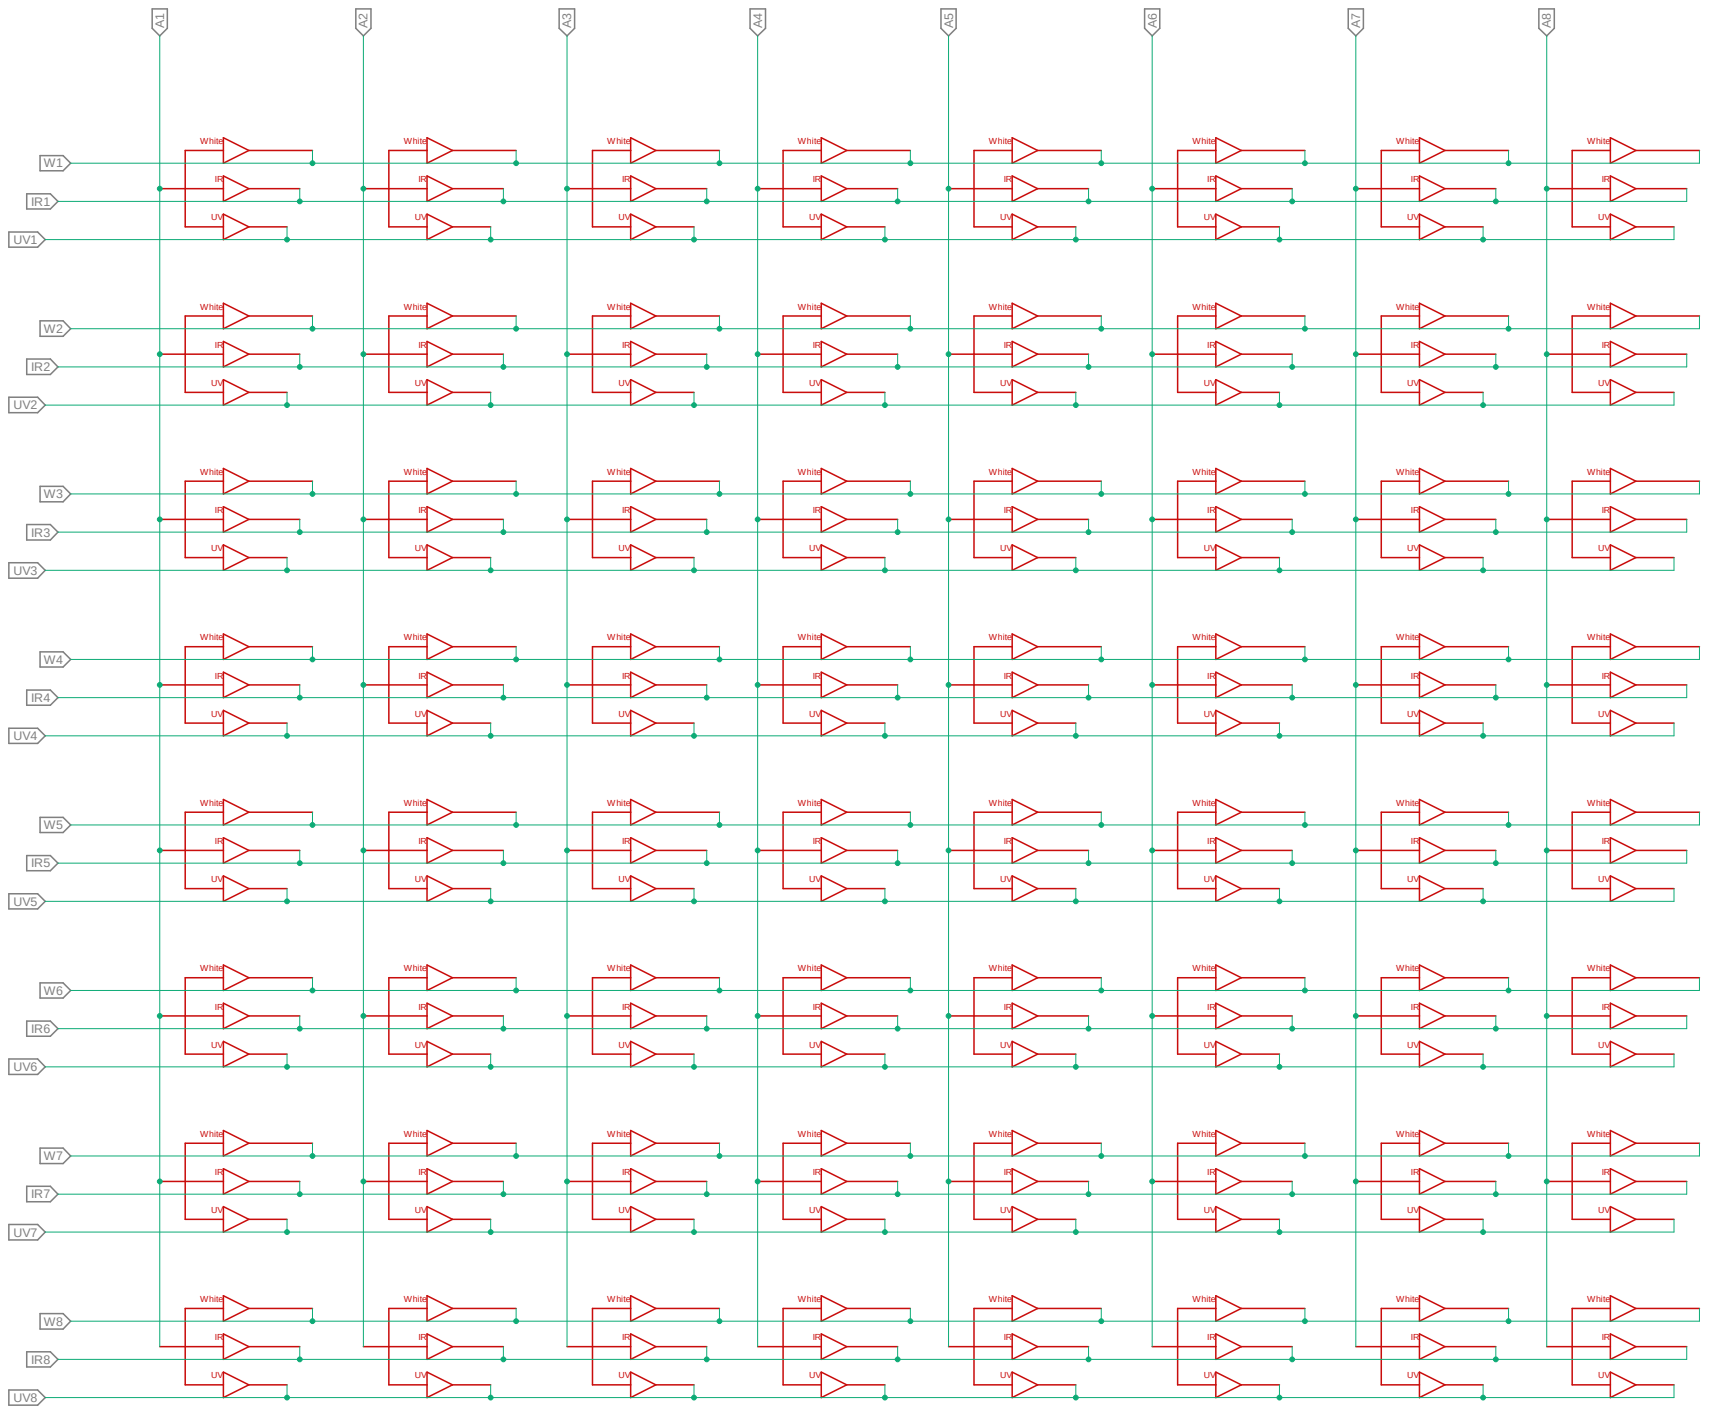
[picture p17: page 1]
White; UV White

UV White

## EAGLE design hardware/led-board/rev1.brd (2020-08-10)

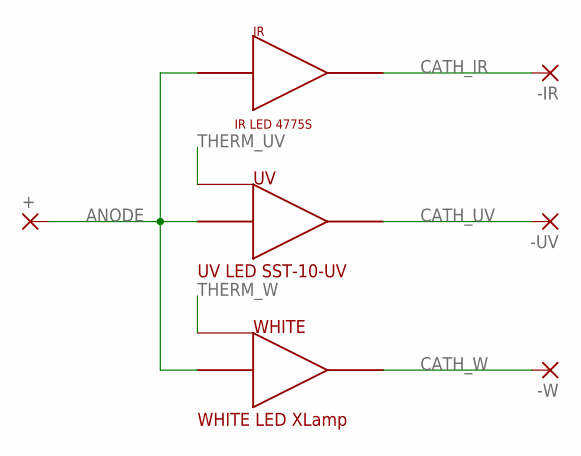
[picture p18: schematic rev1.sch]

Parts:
+: SMD5; SMD2,54-5,08
-IR: SMD5; SMD2,54-5,08
-UV: SMD5; SMD2,54-5,08
-W: SMD5; SMD2,54-5,08
IR: 4775S
UV: SST-10-UV; LED
WHITE: XLAMPXPG2; LED

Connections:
ANODE: +.1, IR.ANODE, IR.ANODE1 (ANODE), IR.ANODE2 (ANODE), UV.ANODE, WHITE.ANODE
CATH_IR: -IR.1, IR.CATHODE, IR.CATHODE1 (CATHODE)
CATH_UV: -UV.1, UV.CATHODE
CATH_W: -W.1, WHITE.CATHODE
THERM_UV: UV.THERM
THERM_W: WHITE.THERM

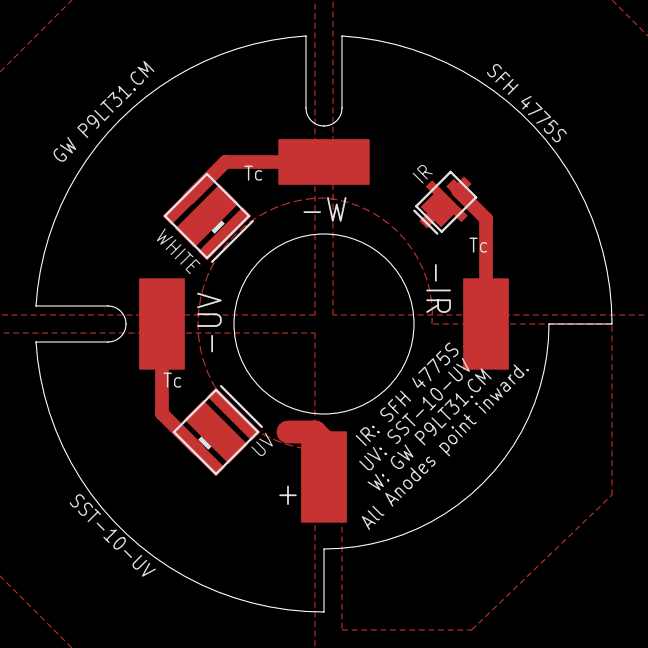
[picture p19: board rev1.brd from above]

Board: 2 copper layers, 32.0 x 32.0 mm, 7 parts (0 on the bottom side), 4 nets.

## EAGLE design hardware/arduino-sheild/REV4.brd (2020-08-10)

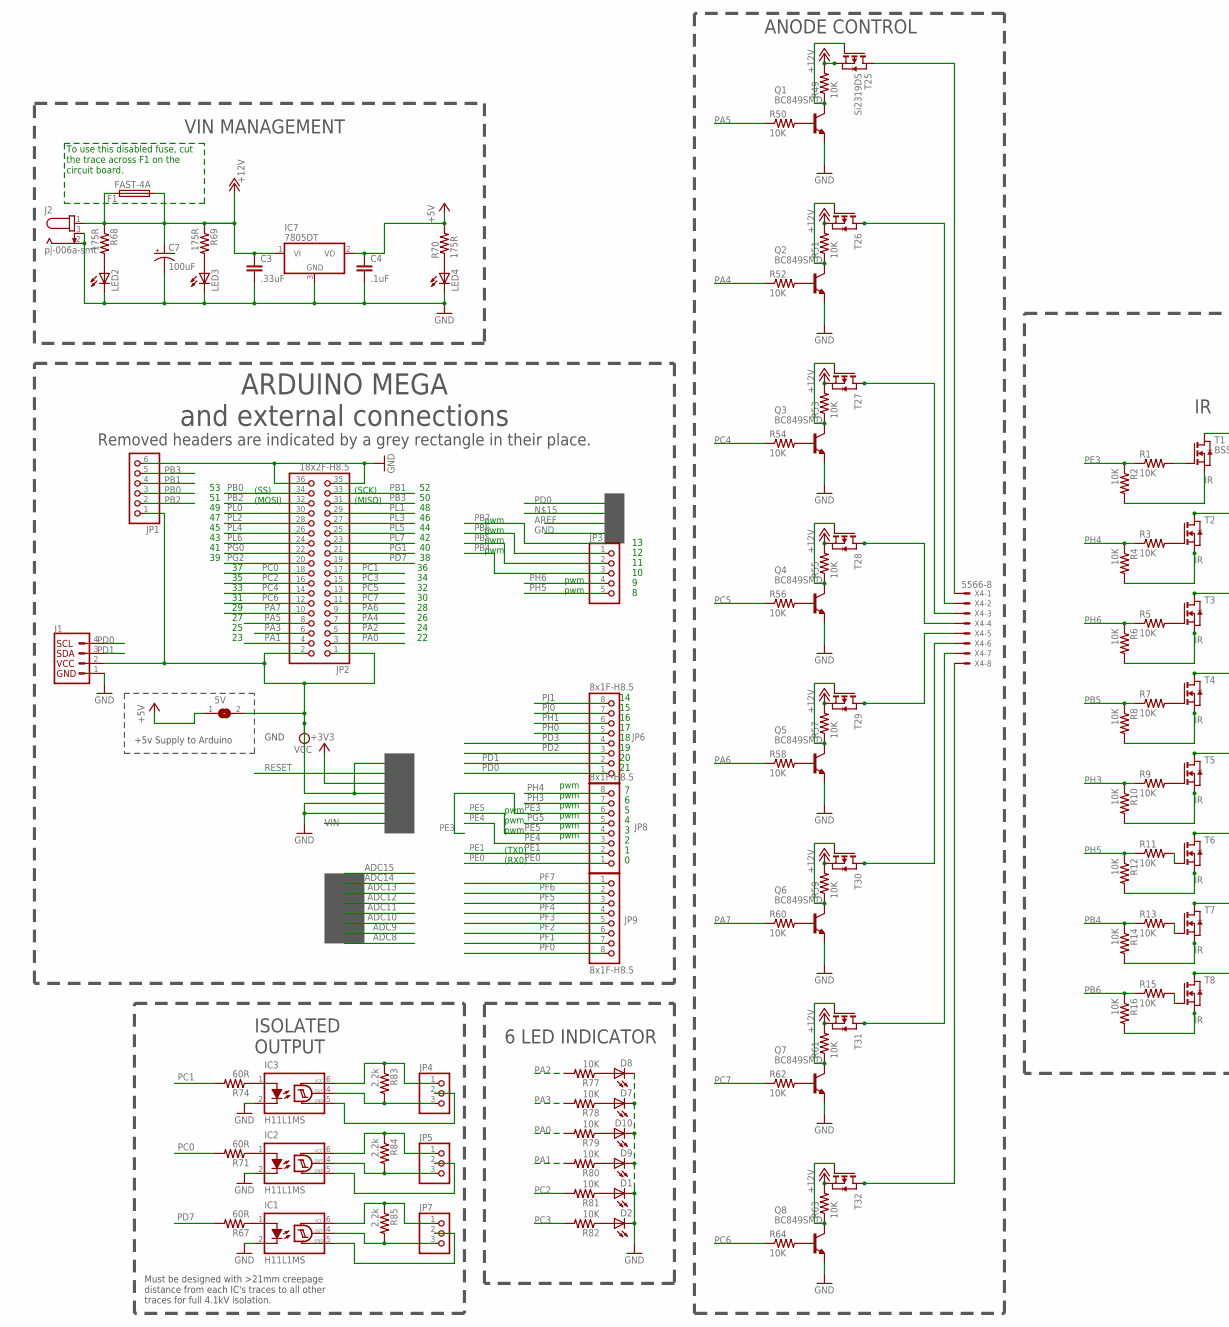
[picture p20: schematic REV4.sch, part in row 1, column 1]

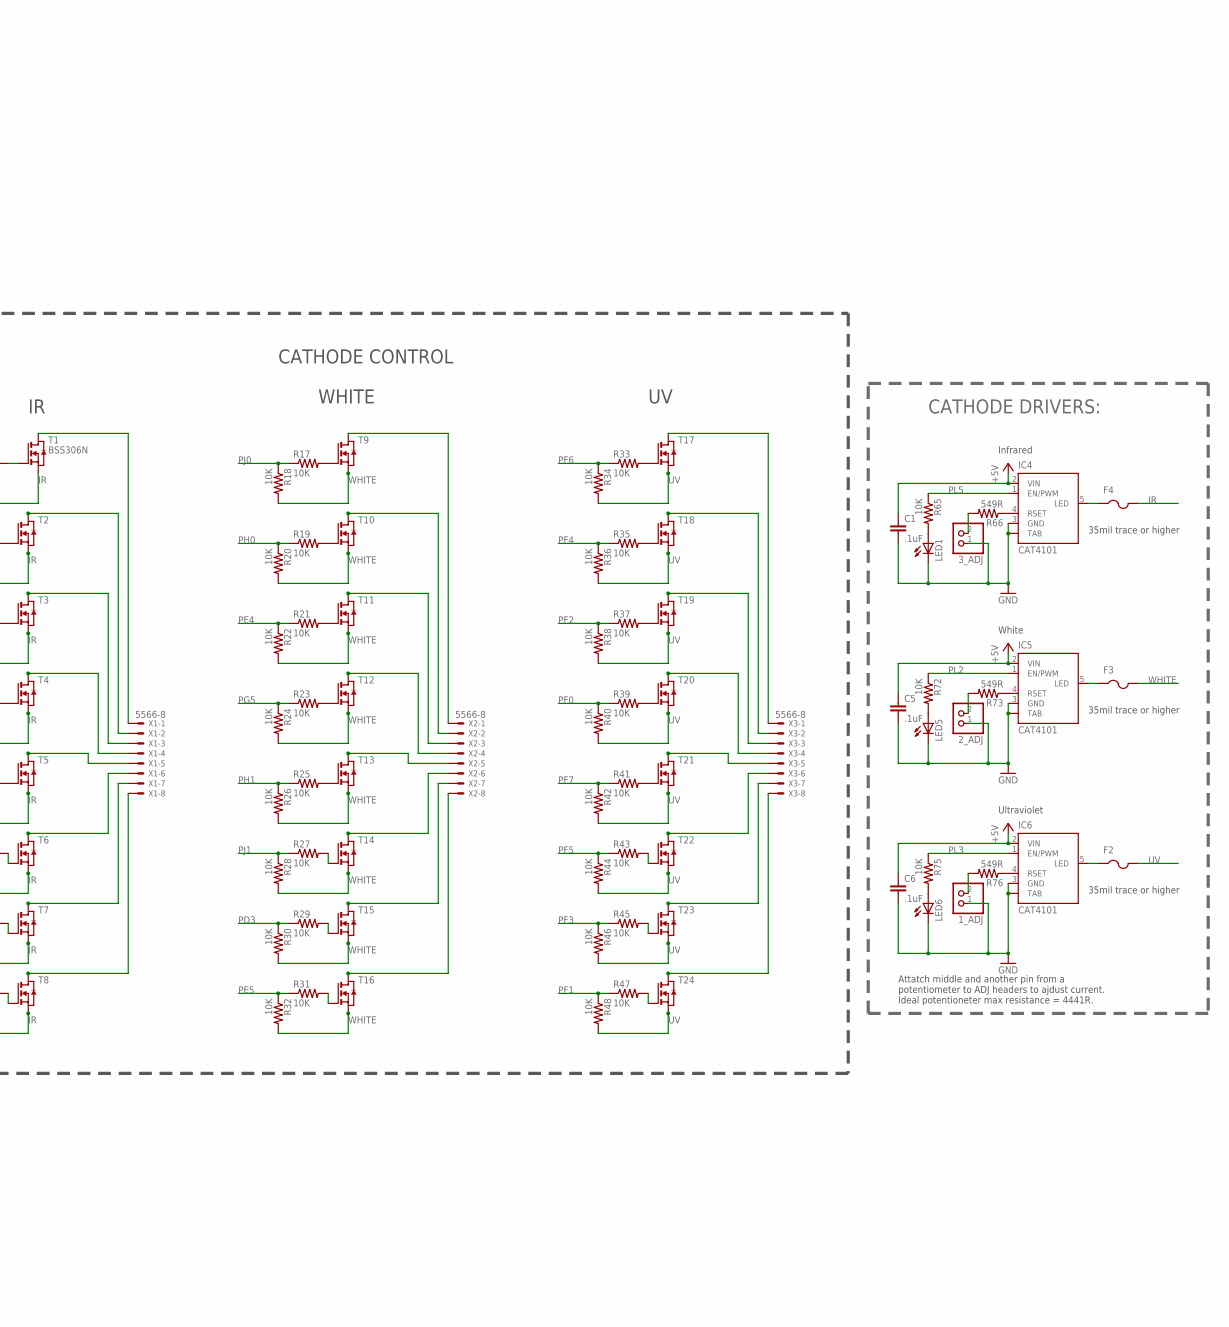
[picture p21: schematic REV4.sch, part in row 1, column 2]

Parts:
1_ADJ, 2_ADJ, 3_ADJ: PINHD-1X2; 1X02
5V: SJ
C1, C4, C5, C6: .1uF; C0805
C3: .33uF; C0805
C7: 100uF; 153CLV-0807
D1, D2, D7, D8, D9, D10: LEDSMT1206; 1206
F1: FAST-4A; FUSE_MF-SMDF050
F2, F3, F4: PTCFUSE-1812; 1812
IC1, IC2, IC3: H11L1MS; DIL6-SMD
IC4, IC5, IC6: CAT4101; TO263_5
IC7: 7805DT; TO252
J1: I2C_STANDARD; 1X04
J2: pj-006a-smt; 69410X210102
JP1: PINHD-1X6; 1X06
JP2: 18x2F-H8.5; 2X18
JP3: PINHD-1X5; 1X05
JP4, JP5, JP7: PINHD-1X3; 1X03
JP6, JP8, JP9: 8x1F-H8.5; 1X08
LED1, LED2, LED3, LED4, LED5, LED6: LEDSMT1206; 1206
Q1, Q2, Q3, Q4, Q5, Q6, Q7, Q8: BC849SMD; SOT23-BEC
R1, R2, R3, R4, R5, R6, R7, R8, R9, R10, R11, R12, R13, R14, R15, R16, R17, R18, R19, R20, R21, R22, R23, R24, R25, R26, R27, R28, R29, R30, R31, R32, R33, R34, R35, R36, R37, R38, R39, R40, R41, R42, R43, R44, R45, R46, R47, R48, R49, R50, R51, R52, R53, R54, R55, R56, R57, R58, R59, R60, R61, R62, R63, R64, R65, R72, R75, R77, R78, R79, R80, R81, R82: 10K; R0805
R66, R73, R76: 549R; R0805
R67, R71, R74: 60R; R0805
R68, R69, R70: 175R; R0805
R83, R84, R85: 2.2k; R0805
T1: BSS306N; SOT-23
T2, T3, T4, T5, T6, T7, T8, T9, T10, T11, T12, T13, T14, T15, T16, T17, T18, T19, T20, T21, T22, T23, T24: NMOSSOT23; SOT-23
T25: Si2319DS; SOT-23
T26, T27, T28, T29, T30, T31, T32: PMOSSOT23; SOT-23
X1, X2, X3, X4: 5566-8

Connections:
+5V: 5V.1, C1.1, C4.1, C5.1, C6.1, IC4.2 (VIN), IC5.2 (VIN), IC6.2 (VIN), IC7.2 (VO), R70.2
+12V: C3.1, C7.+, F1.1, F1.2, IC7.1 (VI), J2.1, R49.2, R51.2, R53.2, R55.2, R57.2, R59.2, R61.2, R63.2, R68.1, R69.1, T25.2 (S), T26.2 (S), T27.2 (S), T28.2 (S), T29.2 (S), T30.2 (S), T31.2 (S), T32.2 (S)
GND: 1_ADJ.1, 2_ADJ.1, 3_ADJ.1, C1.2, C3.2, C4.2, C5.2, C6.2, C7.-, D1.C, D2.C, D7.C, D8.C, D9.C, D10.C, IC1.2 (C), IC2.2 (C), IC3.2 (C), IC4.3 (GND), IC4.TAB, IC5.3 (GND), IC5.TAB, IC6.3 (GND), IC6.TAB, IC7.3 (GND), J1.1, J2.2, J2.3, JP1.6, JP2.35, JP2.36, LED1.C, LED2.C, LED3.C, LED4.C, LED5.C, LED6.C, Q1.E, Q2.E, Q3.E, Q4.E, Q5.E, Q6.E, Q7.E, Q8.E
IR: F4.2, R2.2, R4.2, R6.2, R8.2, R10.2, R12.2, R14.2, R16.2, T1.2 (S), T2.2 (S), T3.2 (S), T4.2 (S), T5.2 (S), T6.2 (S), T7.2 (S), T8.2 (S)
unnamed: LED4.A, R70.1
unnamed: Q2.C, R51.1, T26.3 (G)
unnamed: T26.1 (D), X4.2
unnamed: 1_ADJ.2, R76.2
unnamed: Q1.B, R50.2
unnamed: Q1.C, R49.1, T25.3 (G)
unnamed: T25.1 (D), X4.1
unnamed: D8.A, R77.1
unnamed: 2_ADJ.2, R73.2
unnamed: LED2.A, R68.2
unnamed: Q2.B, R52.2
unnamed: F2.1, IC6.5 (LED)
unnamed: Q3.C, R53.1, T27.3 (G)
unnamed: D1.A, R81.1
unnamed: D7.A, R78.1
unnamed: T27.1 (D), X4.3
unnamed: D10.A, R79.1
unnamed: Q3.B, R54.2
unnamed: F3.1, IC5.5 (LED)
unnamed: Q4.C, R55.1, T28.3 (G)
unnamed: F4.1, IC4.5 (LED)
unnamed: T28.1 (D), X4.4
unnamed: 3_ADJ.2, R66.2
unnamed: Q4.B, R56.2
unnamed: IC4.4 (RSET), R66.1
unnamed: Q5.C, R57.1, T29.3 (G)
unnamed: IC5.4 (RSET), R73.1
unnamed: T29.1 (D), X4.5
unnamed: D2.A, R82.1
unnamed: Q5.B, R58.2
unnamed: Q6.C, R59.1, T30.3 (G)
unnamed: T30.1 (D), X4.6
unnamed: LED3.A, R69.2
unnamed: LED6.A, R75.2
unnamed: LED5.A, R72.2
unnamed: LED1.A, R65.2
unnamed: R1.2, T1.3 (G)
unnamed: D9.A, R80.1
unnamed: IC1.1 (A), R67.1
unnamed: IC2.1 (A), R71.1
unnamed: IC3.1 (A), R74.1
unnamed: Q6.B, R60.2
unnamed: T1.1 (D), X1.1
unnamed: R3.2, T2.3 (G)
unnamed: T2.1 (D), X1.2
unnamed: R5.2, T3.3 (G)
unnamed: T3.1 (D), X1.3
unnamed: R7.2, T4.3 (G)
unnamed: T4.1 (D), X1.4
unnamed: R9.2, T5.3 (G)
unnamed: T5.1 (D), X1.5
unnamed: R11.2, T6.3 (G)
unnamed: T6.1 (D), X1.6
unnamed: R13.2, T7.3 (G)
unnamed: T7.1 (D), X1.7
unnamed: R15.2, T8.3 (G)
unnamed: T8.1 (D), X1.8
unnamed: R17.2, T9.3 (G)
unnamed: T9.1 (D), X2.1
unnamed: R19.2, T10.3 (G)
unnamed: T10.1 (D), X2.2
unnamed: R21.2, T11.3 (G)
unnamed: T11.1 (D), X2.3
unnamed: R23.2, T12.3 (G)
unnamed: T12.1 (D), X2.4
unnamed: R25.2, T13.3 (G)
unnamed: T13.1 (D), X2.5
unnamed: R27.2, T14.3 (G)
unnamed: T14.1 (D), X2.6
unnamed: R29.2, T15.3 (G)
unnamed: T15.1 (D), X2.7
unnamed: R31.2, T16.3 (G)
unnamed: T16.1 (D), X2.8
unnamed: R33.2, T17.3 (G)
unnamed: T17.1 (D), X3.1
unnamed: R35.2, T18.3 (G)
unnamed: T18.1 (D), X3.2
unnamed: R37.2, T19.3 (G)
unnamed: T19.1 (D), X3.3
unnamed: R39.2, T20.3 (G)
unnamed: T20.1 (D), X3.4
unnamed: R41.2, T21.3 (G)
unnamed: T21.1 (D), X3.5
unnamed: R43.2, T22.3 (G)
unnamed: T22.1 (D), X3.6
unnamed: R45.2, T23.3 (G)
unnamed: T23.1 (D), X3.7
unnamed: R47.2, T24.3 (G)
unnamed: T24.1 (D), X3.8
unnamed: Q7.C, R61.1, T31.3 (G)
unnamed: T31.1 (D), X4.7
unnamed: Q7.B, R62.2
unnamed: Q8.C, R63.1, T32.3 (G)
unnamed: T32.1 (D), X4.8
unnamed: Q8.B, R64.2
OK6_GND: IC1.5 (GND), JP7.2
OK6_OUT: IC1.4 (OUT), JP7.3, R85.2
OK6_VCC: IC1.6 (VCC), JP7.1, R85.1
OK7_GND: IC2.5 (GND), JP5.2
OK7_OUT: IC2.4 (OUT), JP5.3, R84.2
OK7_VCC: IC2.6 (VCC), JP5.1, R84.1
OK8_GND: IC3.5 (GND), JP4.2
OK8_OUT: IC3.4 (OUT), JP4.3, R83.2
OK8_VCC: IC3.6 (VCC), JP4.1, R83.1
PA0: JP2.3, R79.2
PA1: JP2.4, R80.2
PA2: JP2.5, R77.2
PA3: JP2.6, R78.2
PA4: JP2.7, R52.1
PA5: JP2.8, R50.1
PA6: JP2.9, R58.1
PA7: JP2.10, R60.1
PB0: JP1.3, JP2.34
PB1: JP1.4, JP2.33
PB2: JP1.2, JP2.32
PB3: JP1.5, JP2.31
PB4: JP3.3, R13.1, R14.1
PB5: JP3.2, R7.1, R8.1
PB6: JP3.1, R15.1, R16.1
PC0: JP2.18, R71.2
PC1: JP2.17, R74.2
PC2: JP2.16, R81.2
PC3: JP2.15, R82.2
PC4: JP2.14, R54.1
PC5: JP2.13, R56.1
PC6: JP2.12, R64.1
PC7: JP2.11, R62.1
PD0: J1.4, JP6.1
PD1: J1.3, JP6.2
PD2: JP6.3
PD3: JP6.4, R29.1, R30.1
PD7: JP2.19, R67.2
PE0: JP8.1
PE1: JP8.2
PE3: JP8.6, R1.1, R2.1
PE4: JP8.3, R21.1, R22.1
PE5: JP8.4, R31.1, R32.1
PF0: JP9.8, R39.1, R40.1
PF1: JP9.7, R47.1, R48.1
PF2: JP9.6, R37.1, R38.1
PF3: JP9.5, R45.1, R46.1
PF4: JP9.4, R35.1, R36.1
PF5: JP9.3, R43.1, R44.1
PF6: JP9.2, R33.1, R34.1
PF7: JP9.1, R41.1, R42.1
PG0: JP2.22
PG1: JP2.21
PG2: JP2.20
PG5: JP8.5, R23.1, R24.1
PH0: JP6.5, R19.1, R20.1
PH1: JP6.6, R25.1, R26.1
PH3: JP8.7, R9.1, R10.1
PH4: JP8.8, R3.1, R4.1
PH5: JP3.5, R11.1, R12.1
PH6: JP3.4, R5.1, R6.1
PJ0: JP6.7, R17.1, R18.1
PJ1: JP6.8, R27.1, R28.1
PL0: JP2.30
PL1: JP2.29
PL2: IC5.1 (EN/PWM), JP2.28, R72.1
PL3: IC6.1 (EN/PWM), JP2.27, R75.1
PL4: JP2.26
PL5: IC4.1 (EN/PWM), JP2.25, R65.1
PL6: JP2.24
PL7: JP2.23
UV: F2.2, R34.2, R36.2, R38.2, R40.2, R42.2, R44.2, R46.2, R48.2, T17.2 (S), T18.2 (S), T19.2 (S), T20.2 (S), T21.2 (S), T22.2 (S), T23.2 (S), T24.2 (S)
UV_SET: IC6.4 (RSET), R76.1
VCC: 5V.2, J1.2, JP1.1, JP2.1, JP2.2
WHITE: F3.2, R18.2, R20.2, R22.2, R24.2, R26.2, R28.2, R30.2, R32.2, T9.2 (S), T10.2 (S), T11.2 (S), T12.2 (S), T13.2 (S), T14.2 (S), T15.2 (S), T16.2 (S)

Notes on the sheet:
pwm
(TX0)
(RX0)
(SS)
(MOSI)
(SCK)
(MISO)
ARDUINO MEGA and external connections
35mil trace or higher
CATHODE DRIVERS:
ISOLATED OUTPUT
ANODE CONTROL
Infrared
White
Ultraviolet
CATHODE CONTROL
GND
Must be designed with >21mm creepage distance from each IC's traces to all other traces for full 4.1kV isolation.
VIN MANAGEMENT
6 LED INDICATOR
Attatch middle and another pin from a potentiometer to ADJ headers to ajdust current. Ideal potentioneter max resistance = 4441R.
+5v Supply to Arduino
Removed headers are indicated by a grey rectangle in their place.
To use this disabled fuse, cut the trace across F1 on the circuit board.
WHITE

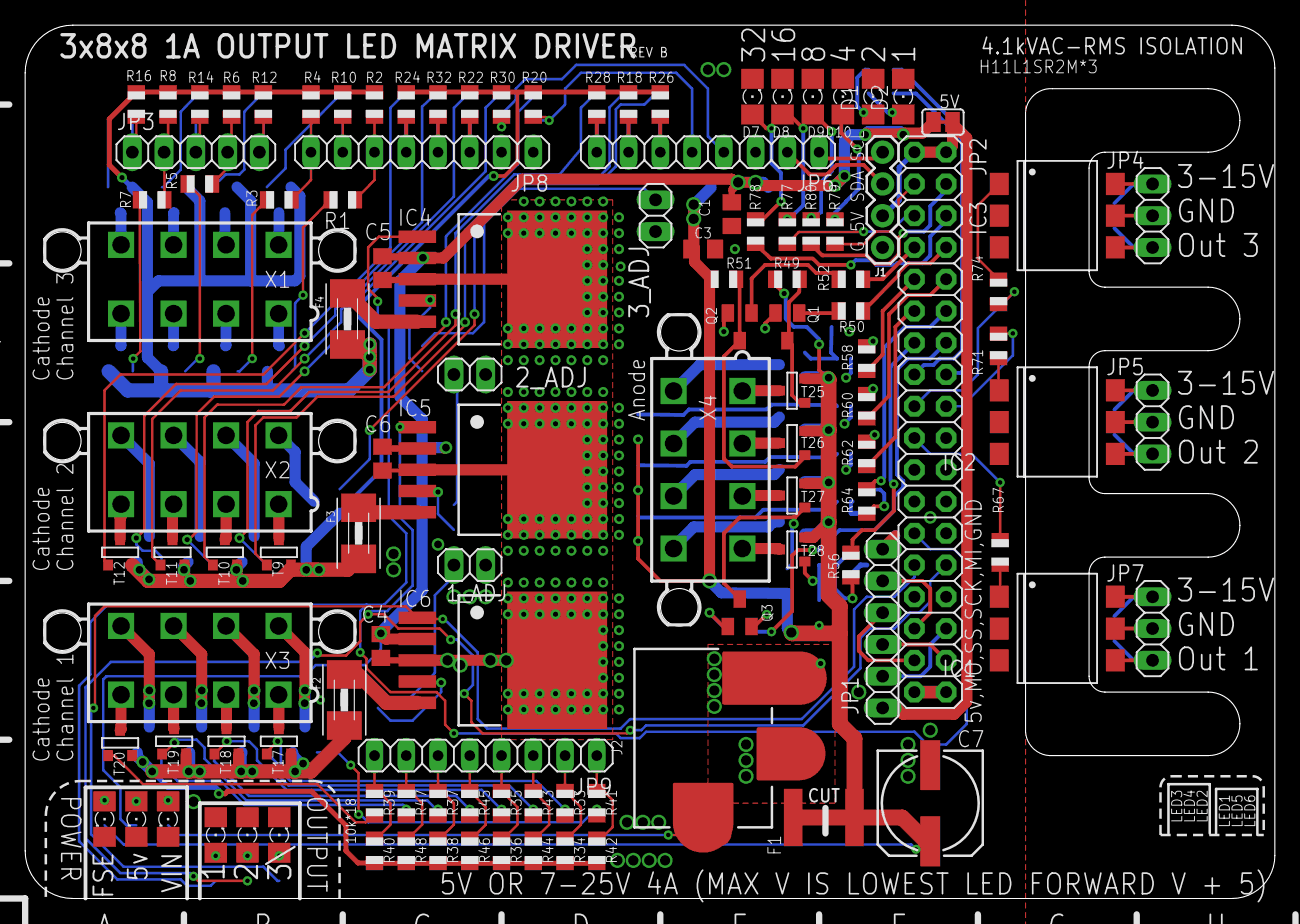
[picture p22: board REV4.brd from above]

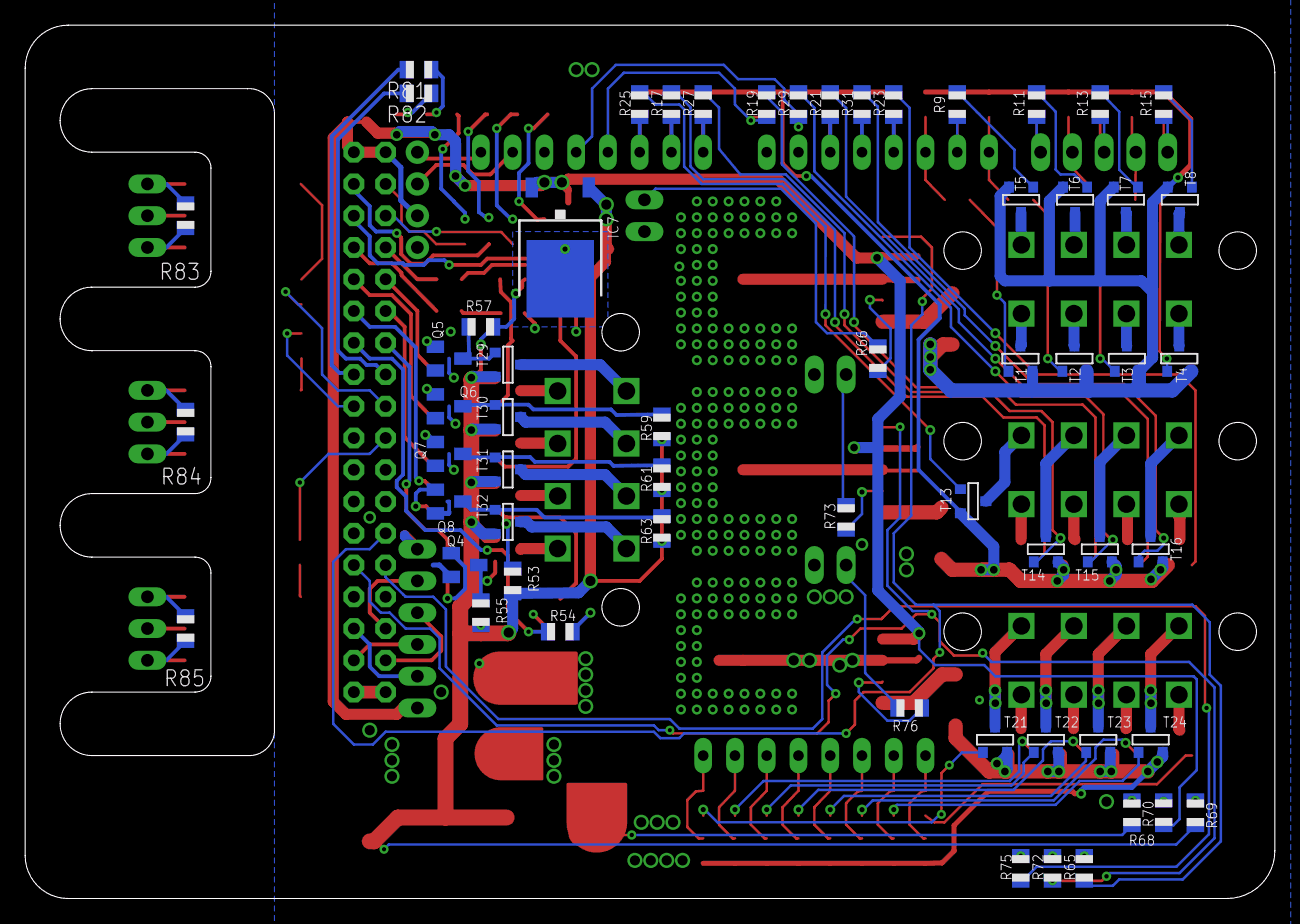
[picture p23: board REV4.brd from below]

Board: 2 copper layers, 99.9 x 69.8 mm, 173 parts (59 on the bottom side), 162 nets.

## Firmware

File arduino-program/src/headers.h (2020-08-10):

/*
 * File Name: 'input119718-34236-1irz0wg.nq0n.h'
 * File Purpose: Header file for all cpp files.
 * By: Nicholas Steele
 */

#include <Arduino.h>

// Libraries
#include "Adafruit_GFX.h"
#include "Adafruit_RA8875.h"
#include "EEPROMAnything.h"
#include <EEPROM.h>
#include <SPI.h>
#include <MemoryFree.h>

/*~~~~~PER-USE SETTINGS~~~~~*/
#define USE_ALT_PIN_SETUP // Uses PD2 in place of PD3 due to an error on the
                          // board. DISABLE IN RELEASE!

#define DEFAULT_BAUD_RATE 115200 // Sets the default baud rate

// Shows "Choose here" in text boxes that need to be set. Might be wanted; this
// was only added for first time use clarification.
// #define CHOOSE_HERE_SHOWN

/*~~~~~VARIABLES~~~~~*/

#define CUSTOM_GREEN 0x2DE0 // A darker, more readable green than RA8875_GREEN.
                            // Good for text, but not so much for anything
                            // thicker.
#define CUSTOM_BLUE 0x31F // A darker, more readable blue than RA8875_CYAN.

// Library only supports hardware SPI at this time
#define RA8875_INT 20
#define RA8875_CS 53
#define RA8875_RESET 21
static Adafruit_RA8875 tft = Adafruit_RA8875(RA8875_CS, RA8875_RESET);
static uint16_t tx, ty;
const PROGMEM int touchDebounceDelay = 200; // Noise delay for touch screen. may
                                            // not be needed, but the first
                                            // display we used had wierd noise
                                            // issues.
static boolean touched = false;
static unsigned long lastTouchTime;
static unsigned int lastTouchCoord[2] = {1025, 1025};
static int cal[4];

static float xScale;
static float yScale;

static unsigned char currentPage;

// Default channel names for display and serial communication use.
#define DEFAULT_CHANNEL_NAME_1 "Ultra Vt"
#define DEFAULT_CHANNEL_NAME_2 "White"
#define DEFAULT_CHANNEL_NAME_3 "InfraRed"

#define CHANNEL_NAME_MAX_CHARACTERS 8 // Should be left at 8, since some boxes
                                      // are designed to fit eightt characters
                                      // and no more.

static char errorChar = 'e';
static char shutterTriggerTypes[2][5] = {"High", "Low"};
static char chNames[3][CHANNEL_NAME_MAX_CHARACTERS + 1];
static char titlesArray[13][17] = {"Home", "Help", "Settings", "LED Order",
	                                 "Single LED", "Profiles", "Help",
	                                 "Column Scan",  "Ring Scan", "Single Ring",
	                                 "Single Column", "Test LEDs", "Positions"};
static char helpArray[13][16] = {"Home", "Help", "Settings", "LED Order",
	                               "Single LED", "Profiles", "Help",
	                               "Column Scan",  "Ring Scan", "Single Ring",
	                               "Single Column", "Test LEDs", "Positions"};

// Stop button/progress bar positions on the display, for patterns
#define STOPBUTTON_W 150
#define STOPBUTTON_H 75
#define STOPBUTTON_X (tft.width() / 2) - (STOPBUTTON_W / 2)
#define STOPBUTTON_Y (tft.height() / 2) - (STOPBUTTON_H / 2)
#define PROGBAR_X STOPBUTTON_X
#define PROGBAR_Y STOPBUTTON_Y + STOPBUTTON_H
#define PROGBAR_W STOPBUTTON_W
#define PROGBAR_H 25

// LED ORDER/PATTERN PAGE VARS
static char ledProfileName[32];
static char shutterProfileName[32];
// char name[32]; // placeholder
static bool listLedProfiles, listShutterProfiles, listChannel,
            listShutterTrigger,
            readingTouch; // Impacts what touch in these area does
static unsigned char ledProfile[3], patternChannel,
                     shutterProfile[3], ringColNum; // used to store vars needed
                                                    // to run LED pattens
static float placeholderFloat;
static unsigned long patternStartTime;
static int xcursortest;
// static bool shutterHigh;

static unsigned char ledList[64]; // List of all LEDs that could be used
static unsigned char ledCount = 64; // Number of LEDs that will be used
static unsigned char ledListPositionCounter = 0;
static unsigned char ledListTextCounter = 0;

static int COUNTnum = 0;

// KEYBOARD
static const unsigned char keyWidth = 70, keyHeight = 50, keySpace = 10,
                           adjust[5] = {0, 0, keyWidth / 2,
	                                      (keyWidth * 6) / 5,
	                                      (keyWidth * 2) / 2}, expansionRatio = 3;
static const char keys[50] = {"0123456789QWERTYUIOPASDFGHJKL#ZXCVBNM>##** ~<"};
static const char shiftKeys[] = {".,/-"};
static bool turnShiftOff;
#define SHIFT_POS_X (keyWidth * 3) + (keySpace * 3) + (keyWidth * \
	                                                     expansionRatio) + \
	(keySpace * (expansionRatio - 1))
#define SHIFT_POS_Y (keyHeight * 4) + (keySpace * 4)

// Shows "Choose here" message in text boxes that may need it.
#ifdef CHOOSE_HERE_SHOWN
static const char chooseHereText = {"Choose here"};
#endif /* ifdef CHOOSE_HERE_SHOWN */

const PROGMEM unsigned char PROFILE_NAME_LENGTH = 32;

static bool q[6] = {0, 0, 0}; // First three: Whether a channel is active
                              // Second three: whether a shutter is active
static uint8_t CHq[3]; // Stores row then column of currently active channel
static unsigned long millisDelay[3]; // Deactivation time for (first 3) LEDs
// (second 3) shutters
// static int shutterLength = 120; // Maximum shutter time in ms

static unsigned long baud = DEFAULT_BAUD_RATE; // Serial Baud Rate; default
                                               // written in

static unsigned long currentMillis; // Used to check runtime in ms

static void (*resetFunc)(void) = 0; // Software reset of arduino.

// char typeList[4][8] = {"Columns", "Rings", "Ring", "Column"};

/*~~~~~Controls LEDs~~~~~*/
class LED_object {
public:
	unsigned char num, r, c; // Stores channel and number of the LED.
	boolean ch1 = false, ch2 = false;

	// Must be set before using.
	// num should be an LID; zero-exlusive and up to 64.
	void setRC();

	void checkRow();

	void trigger(bool mode, unsigned char del, bool shutterHigh =
								 true, unsigned char shutterOnWait = 0);
};

extern LED_object ledArray[192];

/*~~~~~WRITING TO PORTS~~~~~*/
// xxx(port, bit)
#define sbi(x, y) x |= _BV(y) // set bit - using bitwise OR operator
#define cbi(x, y) x &= ~(_BV(y)) // clear bit - using bitwise AND operator
#define tbi(x, y) x ^= _BV(y) // toggle bit - using bitwise XOR operator
#define is_high(x, y) (x & _BV(y) == _BV(y))
// check if the y'th bit of register 'x' is high

/* _BV(a) is a macro which returns the value corresponding to 2 to the power
 * 'a'.
 * Thus _BV(PX3) would be 0x08 or 0b00001000. */

/*~~~~~ARRAY INFO~~~~~
 * Row Pins 1-8: PA5, PA4, PC4, PC5, PA6, PA7, PC7, PC6.
 * Channel 1 Pins 1-8: PF6, PF4, PF2, PF0, PF7, PF5, PF3, PF1
 * Channel 2 Pins 1-8: PJ0, PH0, PE4, PG5, PH1, PJ1, PD3, PE5
 * Channel 3 Pins 1-8: PE3, PH4, PH6, PB5, PH3, PH5, PB4, PB6
 */
#define RR(x)                                                                  \
	((x == 0)                                                                    \
	 ? PORTA                                                                 \
	 : ((x == 1)                                                             \
	    ? PORTA                                                          \
	    : ((x == 2)                                                      \
	       ? PORTC                                                   \
	       : ((x == 3)                                               \
	          ? PORTC                                            \
	          : ((x == 4)                                        \
	             ? PORTA                                     \
	             : ((x == 5)                                 \
	                ? PORTA                              \
	                : ((x == 6) ? PORTC                  \
	                   : PORTC))))))) // Row
// register
// for #
// Row Pins 1-8: PA5, PA4, PC4, PC5, PA6, PA7, PC7, PC6.
#define RB(x)                                                                  \
  \
	((x == 0)                                                                      \
	 ? PA5                                                                    \
	 : ((x == 1)                                                              \
	    ? PA4                                                             \
	    : ((x == 2)                                                       \
	       ? PC4                                                      \
	       : ((x == 3)                                                \
	          ? PC5                                               \
	          : ((x == 4)                                         \
	             ? PA6                                        \
	             : ((x == 5)                                  \
	                ? PA7                                 \
	                : ((x == 6) ? PC7 : PC6))))))) // Row
                                                 // bits
                                                 // for
                                                 // #x
// Channel 1 Pins 1-8: PF6, PF4, PF2, PF0, PF7, PF5, PF3, PF1
#define CH1R(x)                                                                \
	((x == 0)                                                                    \
	 ? PORTF                                                                 \
	 : ((x == 1)                                                             \
	    ? PORTF                                                          \
	    : ((x == 2)                                                      \
	       ? PORTF                                                   \
	       : ((x == 3)                                               \
	          ? PORTF                                            \
	          : ((x == 4)                                        \
	             ? PORTF                                     \
	             : ((x == 5)                                 \
	                ? PORTF                              \
	                : ((x == 6)                          \
	                   ? PORTF                       \
	                   : PORTF))))))) // Channel
                                    // 1
// Register
// for #x
#define CH1B(x)                                                                \
	((x == 0)                                                                    \
	 ? PF6                                                                   \
	 : ((x == 1)                                                             \
	    ? PF4                                                            \
	    : ((x == 2)                                                      \
	       ? PF2                                                     \
	       : ((x == 3)                                               \
	          ? PF0                                              \
	          : ((x == 4)                                        \
	             ? PF7                                       \
	             : ((x == 5)                                 \
	                ? PF5                                \
	                : ((x == 6) ? PF3                    \
	                   : PF1))))))) // Channel
                                  // 1 Bit
                                  // for
                                  // #x.
// Channel 2 Pins 1-8: PJ0, PH0, PE4, PG5, PH1, PJ1, PD3, PE5
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

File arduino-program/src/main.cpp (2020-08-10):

/*~~~~~RTI driver program~~~~~
 * This program is written to drive a Reflectance Tranfromation Imager, or RTI.
 * The Arduino Mega that is programed connects to a purpose-designed sheild
 * which is capable of current-controlling 192 1A LEDs. The intent of the
 * design is to run three seperate sets of rows, referred to as channels here.
 *
 * In our implementation:
 * Channel 1 = Ultraviolet
 * Channel 2 = White
 * Channel 3 = Infrared
 *
 * DIAGNOSTICS MODE:
 * When active, diagnostics mode provides additional information that may be
 * useful to programmers.
 *
 * The top left number (written over the 'Home' button) indicates the remaining
 * SRAM on the device, in bytes. If there are unusal problems with no ovbious
 * solutions, this might be the problem. Under typical conditions, this rarely
 * dips below 4kb of SRAM. This value can be updated by touching anywhere. If
 * the text has a white background, it was updated by the last touch, otherwise
 * it was updated just before the last page was loaded.
 *
 * The bottom left and right corners both contain page information. The bottom
 * left has the current page written on it, and the bottom right has the
 * previous visited page on it. These are mainly for troubleshooting name arrays
 * and Help pages.
 *
 * The top left rarely carries any information.
 *
 * Circles at tap locations indicate where a tap was detected, and the color can
 * be used to indicate how that tap is handled. The colors are as follows:
 * RED: The device is not in any loop. This should only be visible on pages with
 *      buttons that have simpler functions (such as changing a page)
 * BLUE: The device is in a loop, but can be escaped by pressing 'Home' or
 *     'Help'. This color is usually found on a page with buttons with complex
 *      functions.
 * CYAN: The device is in a loop that can only be escaped by following though on
 *      an action. Usually this is is used when waiting for an entry on a
 *      number pad or a stop button (stop button boxes will disapear after a set
 *      time.)
 *
 */

#ifndef HEADERS_H
#define HEADERS_H
#include <headers.h>
#endif // ifndef HEADERS_H

static LED_object ledArray[192]; // LED objects

/*~~~~~COMMAND DEFINITIONS~~~~~*/
void waitForResponse();

void checkSerial();

void setPinModes();

void setupLEDs();

void assignCHNames();

/*
 * This is a placeholder object, used to make ledArray a globally accessible
 * object array.
 */

LED_object ledPlaceholder(unsigned char num) {
	return ledArray[num];
} // ledPlaceholder
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

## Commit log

2020-08-10 Initial commit with files
    [REV4.brd, REV4.sch, led-variants.csv, main-board-bom.csv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]
2020-08-11 Update README.md
    Started documentation of boards
2020-08-12 Delete led-array.md
    Moved to wiki
2020-08-12 Delete led-board.md
    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
2020-09-02 Change newlines
    [led-variants.csv]

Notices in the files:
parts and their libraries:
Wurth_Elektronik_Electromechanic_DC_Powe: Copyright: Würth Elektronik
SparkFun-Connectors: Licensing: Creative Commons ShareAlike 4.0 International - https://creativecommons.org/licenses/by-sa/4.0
